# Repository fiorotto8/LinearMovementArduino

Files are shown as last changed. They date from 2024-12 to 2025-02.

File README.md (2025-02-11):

# Moving stage for Source and TPH sensor

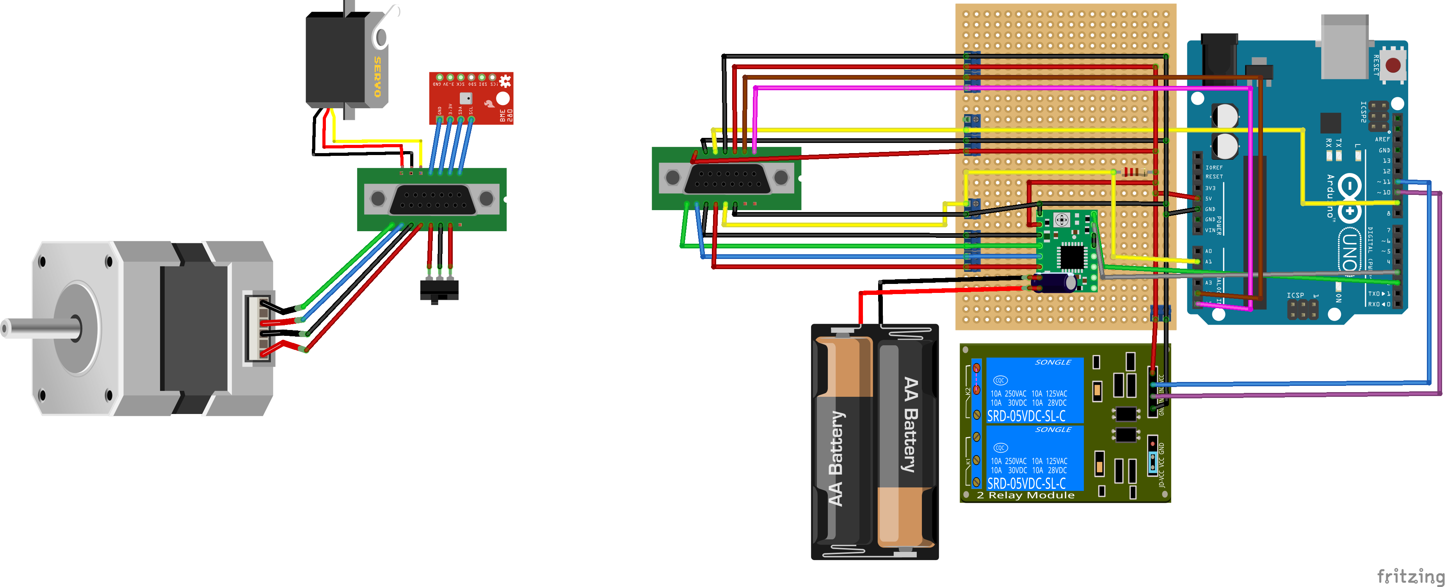
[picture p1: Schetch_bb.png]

NB: the image of the AA battery pack is referred to the 24V DC power supply!

## Basic instructions
Send a byte through serial port to Arduino

- **R**: Arduino replies with *temperature;pressure;humidity;VOC* [K,Pa,%,$\Omega$]
- **G**: Get the position of the stage with respect to the *zero*. Possible only after calibration
- **C**: do the calibration and stays to the *zero* position
- **P**: Set the position in mm from the *zero*. After that a prompt will ask you the position in mm. Not working without calibration. It is not possible to go to *zero* with this function, use the calibration procedure.
- **Z**: To send during any movement to stop it prematurely
- **W**: To return the detector where the Arduino is connected (KEG or MANGOlino)
- **Y**: Return if the calibration has already been done
- **K**: Reset the Arduino, equivalent to click the reset button
- **T**: Excite the Relays to connect the Motor power supply to the 220V
- **U**: Dexcite the Relays to disconnect the Motor power supply to the 220V
- **S**: Get Relays status
- **L**: Set the Source holder Servomotor position. After that a prompt will ask you the position: 4 positions are possible where pos1 correspond to angle 0° and pos4 to angle 270°

The Arduino will print a lot of stuff on the Serial, however only when a return code, *E followed b a number* is given an operaation is finished:

- **E0**: no error, operation completed succesfully
- **E1**: "Calibration not done, I will not move!" if the P command is sent before the calibration
- **E2**: Calibratioin interrupted by Z command
- **E3**: During servo positioning a wrong poition was given
- **E4**: Timeout during servo positioning
- **E5**: Timeout during stepper positioning
- **E6**: Impossible movement for the stepper, negative position of greater than 110
- **E7**: P0 is not allowed use Calibration instead
- **E8**: position movement stopped by Z command
- **E9**: 'Z' command received when no operation was ongoing

## TPH sensor

The sensor is a BME 680 that measure Temperature, pressure, humidity and VOC (volatile organic compounds).
Arduino talks to it via I2C. the sensor requires +5V and GROUND. **SDA and SCL are respectively connected to A4 and A5 analog input.**
| Wire Name      | Pin On Arduino
| :---:        |    :----:   |
| VCC      | Anywhere 5V       |
| GND   | Anywhere GND        |
| SDA   | A4        |
| SCL   | A5        |

## Moving stage

The stage is moving via a bipolar stepper motor. A switch on one edge of the guide is used to get the *zero* position via calibration procedure.
The Switch is read by A1 analog Pin and it triggers when the reading is less than 500.
The motor driver A4988 should be connected both to 5V and the 24V DC power supply.

Here the mapping of the cable from the motor to the controller.
| Name on A4988      | Other name | Color of the wire     |
| :---:        |    :----:   |          :---: |
| 1B      | A+       | Black   |
| 1A   | A-        | <span style="color:green">Green</span>      |
| 2A   | B-        | <span style="color:blue">Blue</span>      |
| 2B   | B+        | <span style="color:red">Red</span>      |

Remember to connect in parallel to the 24V a 100$\mu$F capacitor to avoid to burn the controller.
We selected 1.7 k$\Omega$ for the resistance for the switch.

A recent feature is the adding of 2 relays that remove the power from the motor power supply to avoid noise to the PMT.

## Mapping of the 15pin parallel cable for the Vessel feedthroug

To enter in the vacuum vessel we used some connector with 15 pins. Here the mapping:

| Pin Number      | Connection |
| :---:        |    :----:   |
| 1      | <span style="color:green">1A</span>       |
| 2      | <span style="color:blue">2A</span>       |
| 3      | 1B       |
| 4      | <span style="color:red">2B</span>       |
| 5      | Switch -       |
| 6      | Switch Ground       |
| 7      | Switch +       |
| 8      | NC      |
| 9      | VCC 5V (Servo)       |
| 10      | GND (Servo)       |
| 11     | Servo Controller       |
| 12      |  GND (BME 680)      |
| 13      | VCC 5V (BME680)       |
| 14      | SDA       |
| 15      | SCL       |

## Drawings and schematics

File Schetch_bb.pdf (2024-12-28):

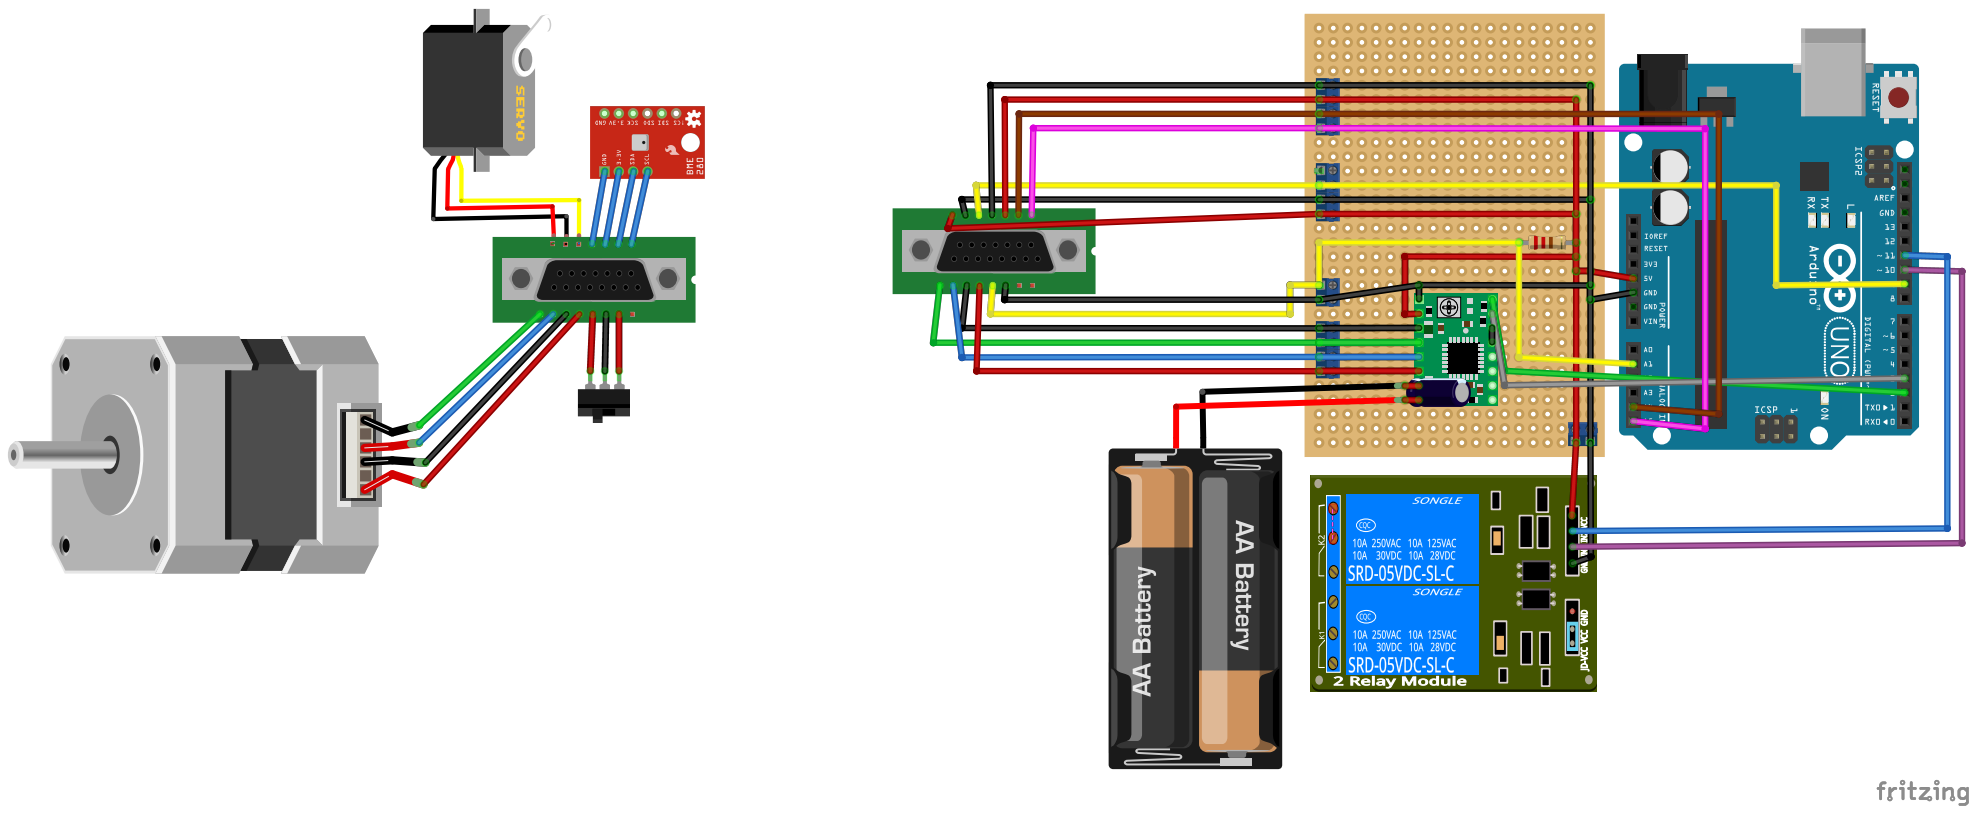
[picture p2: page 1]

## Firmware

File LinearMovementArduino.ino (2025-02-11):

#include <Wire.h>
#include <SPI.h>
#include <Adafruit_Sensor.h>
#include "Adafruit_BME680.h"
#include <Servo.h>

//Function to software reset
void(* Reset)(void) = 0;

// Pin definitions for the stepper motor and switch
const int SwitchPin = 4; // Pin connected to the switch
const int DirPin = 2;    // Direction control pin for stepper motor
const int StepPin = 3;   // Step control pin for stepper motor
//int enablePin = 5;    // ENABLE pin
const int relay1Pin = 10;    // Relay 1 pin
const int relay2Pin = 11;    // Relay 2 pin

Servo myServo;
int periodTimeout=5000;

bool relayStatus;

// Variables to store the status of the switch and motor direction and step
int SwitchStatus, DirStatus, StepStatus;

// Stepper motor configuration
const int stepsPerRevolution = 200; // Number of steps per full revolution of motor
const int WaitTimeSpeed = 1;        // Delay time for motor control, in milliseconds
const int StepForMm = 200;          // Number of steps per millimeter of movement
float xPos;                   // Current position of the motor
bool CalDone = 0;             // Flag indicating if calibration is done


// Pin for reading analog values from a switch (if used)
const int AnalogSwitchPin = A1;

// Function to excite the relays i.e. powering ON the AC/DC converter
bool ExciteRelays(){
  digitalWrite(relay1Pin, LOW);
  digitalWrite(relay2Pin, LOW);
  return true;
}

// Function to deexcite the relays i.e. powering OFF the AC/DC converter
bool DexciteRelays(){
  digitalWrite(relay1Pin, HIGH);
  digitalWrite(relay2Pin, HIGH);
  return false;
}

// Function to calibrate the zero position of the stepper motor
float ZeroCal() {
  // Set the spinning direction clockwise
  digitalWrite(DirPin, HIGH);

  bool digi_zero;
  int anal_zero;
  // Move motor until the switch is activated or a 'Z' (ASCII 90) is received on Serial
  //while (digitalRead(SwitchPin) == 1 && Serial.read() != 90) {
  while (true) {

    digi_zero = digitalRead(SwitchPin);
    anal_zero = analogRead(AnalogSwitchPin);
    //Serial.println(digi_zero);
    //CSerial.println(anal_zero);
    int incoming = Serial.read();
    if (incoming == 90){ // Stop if 'Z' is received
       Serial.println("Z received stopping calibration..."); 
       return 0;
    }
      // If we got *some* other character (not -1), ignore it and dump the buffer
    else if (incoming != -1) {
      // Dump any extra characters waiting in the buffer
      while (Serial.available() > 0) {
        Serial.read();
      }
      Serial.println("Ignoring unexpected message, dumping buffer...");
    } 
    //if (digi_zero == 0){ // Stop if switch is activated
    //  Serial.println("Switch Pin hit endpoint found...");
    //  break;
    //} 

    if (anal_zero < 500){ // Stop if switch is activated
      Serial.println("Switch Pin hit endpoint found...");
      break;
    } 

    digitalWrite(StepPin, HIGH);
    delay(WaitTimeSpeed);
    digitalWrite(StepPin, LOW);
    delay(WaitTimeSpeed);
  }
  delay(100);

  // Move motor away from the switch to a specified offset
  float diffX = 5.5; // Offset distance in mm
  int stepsToDo = abs(diffX * StepForMm); // Convert offset to steps
  digitalWrite(DirPin, LOW); // Change direction
  for (int i = 0; i < stepsToDo; i++) {
    digitalWrite(StepPin, HIGH);
    delay(WaitTimeSpeed);
    digitalWrite(StepPin, LOW);
    delay(WaitTimeSpeed);
  }
  return 1;
}

// Function to return the current position of the motor
float getXPos() {
  return xPos;
}

// Function to move the motor to a specified position
int SetPos(float &realX, float fakeX) {
  float diffX; // Difference between current and target position
  int stepsToDo = 0; // Number of steps to move
  diffX = fakeX - realX; // Calculate the difference in position

  // Check for boundary conditions
  if (fakeX > 110 || fakeX < 0) {
    Serial.println("Impossible movement");
    return 6;
  }
  else if (fakeX == 0){
    Serial.println("To go to 0 position use Cal function instead");
    return 7;
  }

  // Set motor direction based on the position difference
  if (diffX < 0) digitalWrite(DirPin, HIGH);
  else if (diffX > 0) digitalWrite(DirPin, LOW);
  else if (diffX == 0) {
    Serial.println("Already in position");
    return 0;
  }

  stepsToDo = abs(diffX * StepForMm); // Convert position difference to steps
  //Serial.println(stepsToDo);

  // Move the motor the calculated number of steps
  int iter = 0;
  /*
  Serial.println("stepsToDo - iters");
  Serial.print(stepsToDo);
  Serial.print(" ");
  Serial.println(iter);
  */
  for (int i = 0; i < stepsToDo; i++) {
    digitalWrite(StepPin, HIGH);
    delay(WaitTimeSpeed);
    digitalWrite(StepPin, LOW);
    delay(WaitTimeSpeed);

    int anal_pos = analogRead(AnalogSwitchPin);

    int incoming = Serial.read();
    if (incoming == 90){ // Stop if 'Z' is received
       Serial.println("Z received stopping movement..."); 
       return 8;
    }
    // If we got *some* other character (not -1), ignore it and dump the buffer
    else if (incoming != -1) {
      // Dump any extra characters waiting in the buffer
      while (Serial.available() > 0) {
        Serial.read();
      }
      Serial.println("Ignoring unexpected message, dumping buffer...");
    }
    /*
    if (digitalRead(SwitchPin) == 0){ // Stop if switch is activated
      Serial.println("Switch Pin hit stopping movement...");
      break;
    } 
    */

    if (anal_pos < 500 ){ // Stop if switch is activated
      Serial.println("Switch Pin hit stopping movement...");
      break;
    }
    /*
    Serial.println("stepsToDo - iters");
    Serial.print(stepsToDo);
    Serial.print(" ");
    Serial.println(iter);
    */
    iter++;
  }

  // Update the real position of the motor
  float temp = realX;
  float nvm = ((float)iter / (float)StepForMm);
  if (diffX < 0) temp = temp - nvm;
  else if (diffX > 0) temp = temp + nvm;
  realX = temp;
  return 0;
}

// Initialization of BME680 sensor
Adafruit_BME680 bme; // I2C
int incomingByte = 0; // Variable to store incoming serial data


// Setup function, runs once at startup
void setup() {
  Serial.begin(115200); // Start serial communication at 115200 baud rate

  // Setup pins for the stepper motor and switch
  pinMode(SwitchPin, INPUT);
  pinMode(DirPin, OUTPUT);
  pinMode(StepPin, OUTPUT);
  //pinMode(enablePin, OUTPUT);
  pinMode(relay1Pin, OUTPUT);
  pinMode(relay2Pin, OUTPUT);

  // Initialize BME680 sensor
  if (!bme.begin()) {
    Serial.println(F("Could not find a valid BME680 sensor, check wiring!"));
    //while (1); // Uncomment to halt if sensor is not found
  }

  // Set up oversampling and filter initialization for BME680
  bme.setTemperatureOversampling(BME680_OS_8X);
  bme.setHumidityOversampling(BME680_OS_2X);
  bme.setPressureOversampling(BME680_OS_4X);
  bme.setIIRFilterSize(BME680_FILTER_SIZE_3);
  bme.setGasHeater(320, 150); // Set heater temperature and duration

  //Deexcite realys!
  relayStatus=DexciteRelays();
  // INITIALLY disable the driver
  //digitalWrite(enablePin, HIGH);

}

// Main loop function, runs repeatedly
void loop() {
  // Check if data is available on the serial port
  if (Serial.available() > 0) {
    incomingByte = Serial.read(); // Read the incoming byte

    // Uncomment for degub about message received
    //Serial.print("Command received is: ");
    //Serial.println(incomingByte);
    //delay(100);

    //Move source servomotor
    if (incomingByte == 76) { // 'L' command
      int anglePos=0;
      Serial.println("Write Servo Position (1, 2, 3 or 4)");
      unsigned long startMillis=millis();
      unsigned long currentMillis=millis();
      while (anglePos==0){
        anglePos = Serial.readString().toInt();
        currentMillis=millis();
        if ((currentMillis-startMillis)>periodTimeout){
          Serial.println("Timeout for Servo positioning");
          Serial.println("E4");
          return;
        }
      }
      int angle=-1;
      if (anglePos==1){angle=0;}
      else if (anglePos==2){angle=60;}
      else if (anglePos==3){angle=125;}
      else if (anglePos==4){angle=270;}
      else {
        Serial.println("Servo position invalid");
        Serial.println("E3");
        return;
      }
      myServo.attach(9, 500, 2500);
      myServo.write(angle);
      delay(1000);
      Serial.print("Servo moved to Pos");
      Serial.print(anglePos);
      Serial.print(" i.e. angle ");
      Serial.println(angle);
      myServo.detach();
      Serial.println("E0");
    }

    //Software reset the board
    if (incomingByte == 75) { // 'K' command
      Serial.println("Resetting Arduinio...");
      Serial.println("E0");
      delay(100);
      Reset();
    }    

    // Handle BME sensor reading
    if (incomingByte == 82) { // 'R' command
      unsigned long endTime = bme.beginReading();
      if (endTime == 0) {
        Serial.println(F("Failed to begin reading :("));
        return;
      }
      if (!bme.endReading()) {
        Serial.println(F("Failed to complete reading :("));
        return;
      }
      // Output sensor readings
      Serial.print(bme.temperature + 273.15); // Convert to Kelvin
      Serial.print(";");
      Serial.print(bme.pressure);
      Serial.print(";");
      Serial.print(bme.humidity);
      Serial.print(";");
      Serial.println(bme.gas_resistance);
      Serial.println("E0");
    }

    // Handle calibration
    if (incomingByte == 67) { // 'C' command
      // Initially ecite relays and enable the driver
      Serial.println("Excite relays...");
      relayStatus=ExciteRelays();
      delay(2000);
      //digitalWrite(enablePin, LOW);
      //delay(2000);
      //start calibtion
      Serial.println("Calibrating...");
      //xPos = ZeroCal();
      //CalDone = 1;

      CalDone = ZeroCal();
      // Disable the driver and deectire realys
      Serial.println("Dexcite relays...");
      delay(100);
      relayStatus=DexciteRelays();
      delay(2000);
      if (CalDone == 1){
        xPos=0;
        Serial.println("Calibration Done!");
        Serial.println("E0");
      }
      else{
        Serial.println("Calibration Interrupted!");
        Serial.println("E2");
      }
    }

    // Position check
    if (incomingByte == 71) { // 'G' command
      Serial.print("Current position: ");
      Serial.println(getXPos());
      Serial.println("E0");
    }

    // fake 'Z' press
    if (incomingByte == 90) { //'Z' command}
      Serial.println("Z received for no reason");
      Serial.println("E9");
    }


    // Realy Status check
    if (incomingByte == 77) { // 'M' command
      Serial.print("Relays excited: ");
      Serial.println(relayStatus);
      Serial.println("E0");
    }

    // Check if calibration has been done
    if (incomingByte == 89) { // 'Y' command
      Serial.print("Calibration: ");
      Serial.println(CalDone);
      Serial.println("E0");
    }

    // Identify device
    if (incomingByte == 87) { // 'W' command
      Serial.println("KEG");
      Serial.println("E0");
    }

    // Get Relays Status
    if (incomingByte == 83) { // 'S' command
      Serial.print("Relays are: ");
      Serial.println(relayStatus);
      Serial.println("E0");
    }

    // Excite relays
    if (incomingByte == 84) { // 'T' command
      Serial.print("Relays excited ");
      Serial.println(relayStatus=ExciteRelays());
      Serial.println("E0");
    }

    // Dexcite relays
    if (incomingByte == 85) { // 'U' command
      Serial.print("Relays deexcited ");
      Serial.println(relayStatus=DexciteRelays());
      Serial.println("E0");
    }
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

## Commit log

2023-10-22 first version of moving motor
2023-10-22 First version with working motor and serial control
2023-12-11 Done readme and schetch beacuse David was too busy
    [Schetch.fzz]
2023-12-18 slight changeschetch updated. Added the info about the detector
    [Schetch.fzz]
2024-01-12 2 new functions added. W for whoami func and Y to know if calibration was done
2024-01-22 Correct the drawings
    [Schetch.fzz]
2024-01-22 Added teh ENABLE PIN control to remove EM noise
    [Schetch.fzz]
2024-03-04 Added "PANDA" printout to match with rpcServer
2024-12-27 Addeed Servomotor code
    [Schetch.fzz]
2024-12-28 Final version with servo, realy and new schematics
    [Schetch.fzz]
